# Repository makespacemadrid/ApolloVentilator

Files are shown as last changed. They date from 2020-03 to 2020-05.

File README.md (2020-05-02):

# ApolloVentilator

Information: Checkout our [wiki](https://github.com/makespacemadrid/ApolloVentilator/wiki)

### Schematic
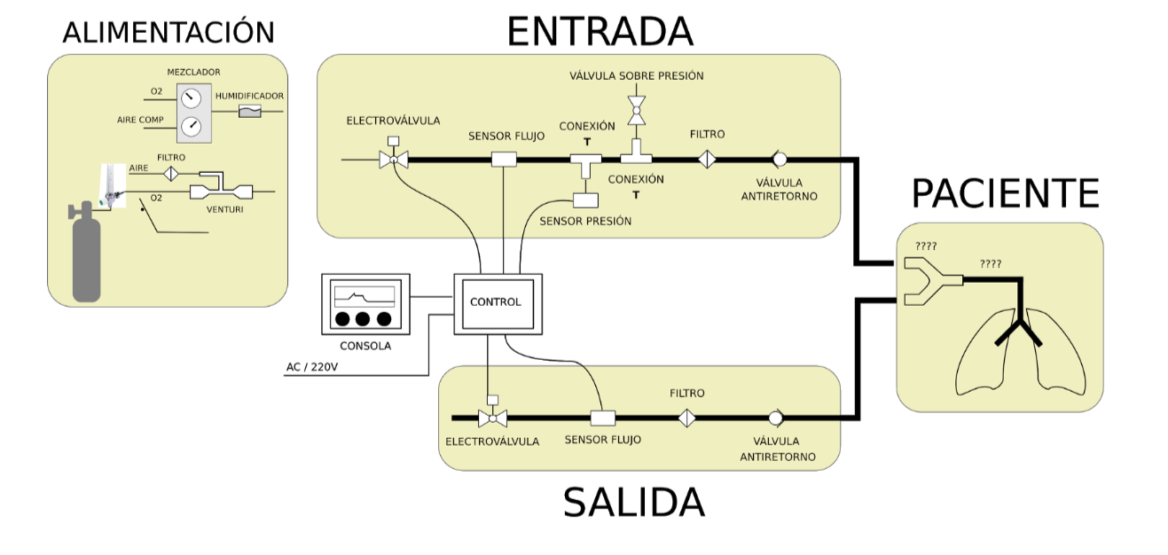
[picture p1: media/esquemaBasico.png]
Schematic


### Prototype 1 @ MakeSpace Madrid
Prototype1

### Prototype 2 @ Miguel's Workshop
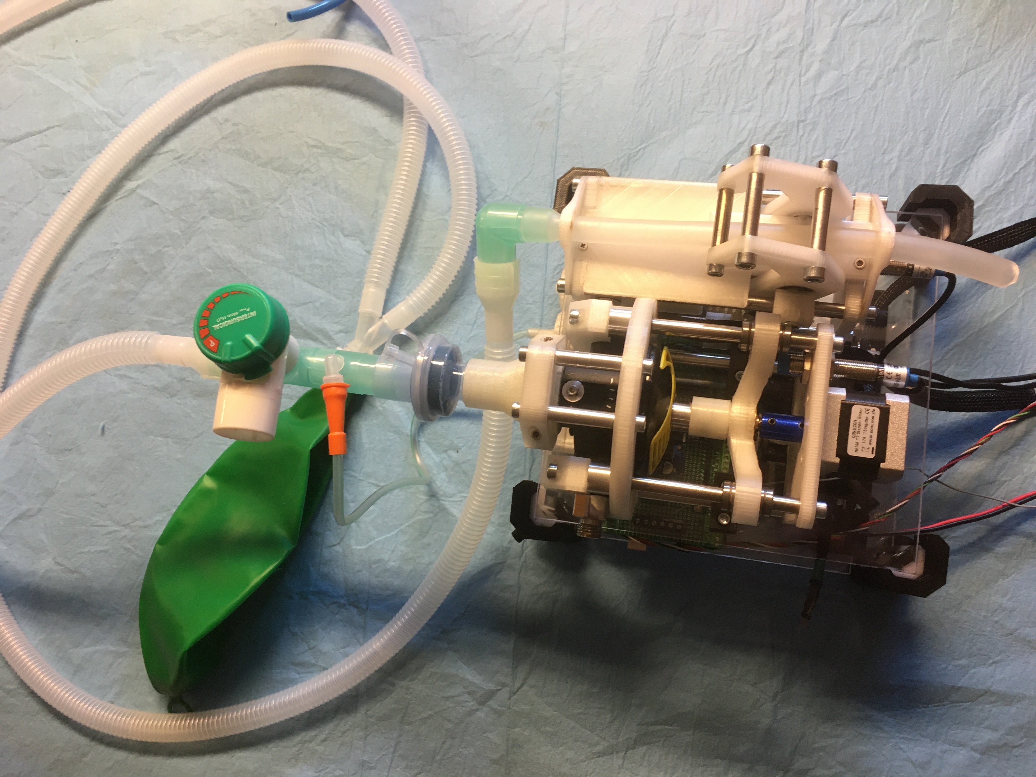
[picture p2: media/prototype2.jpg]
Prototype2


## Getting started

### Linux

```
$ apt-get install libcairo2-dev libgirepository1.0-dev python3-cairo-dev
```

### Mac

```
$ brew install pygobject3 gtk+3 libnotify
```

### App (Python 3)

From ```./gui```

Install system dependencies (Debian-based):

```
$ pip install -r requirements.txt
$ ./main.py
```

## Requirements:
2 ventilators mode
* Pressure Regulated Volume Controlled (PCV): set pressure delivered during period of inspiration. The voume measured is shown as data on display. 
* Volume Regulated Pressure controlled (VCV): The tidal volume is set and it adapts the pressure to the lowest. Here the important data are: tidal volume, upper alarm and lower current volume. Useful parameters: tidal volume, respiratory rate. There is a limit pressure and during inspiration period.

If patient stops breathing, there is a failsafe that set to mandatory breathing when it's detected.

During inspiration:

* Inspiration pressure: The plateau pressure is adjusted to volume hard limit (32 cmH2O by default, and could increate to 70cmH2O)
* Peak pressure: 2cmH2O greater than plateau.
* VCV pressure limit (15-40cm2 with increments of 5)
* Failsafe valve that opens always at 80cmH20 (or lower)

* PEEP: 5-10 with increments of 5. The circuit must be pressured.
* IE ratio: 1:1, 1:2, 1:3
* Respiratory rate: 10-30 bpm with increments of 2.
* Tidal volume: 40ml +-10, 350 +-50, 250-600 +-50,up to 8000. 
* Weight body and volume calculated based on 6ml/kg.

## Alarms

* Gas failure
* Electricity failure
* Machine switched off
* Inspiration pressure exceeded
* Inspiration pressure not achieved
* PEEP pressure not achieved
* Tidal volume not achieved
* Tidal volume exceeded
* Resistance: peak pressure - plateau pressure > 2cmH2O
* Compliance
* Volume Leakage

## Monitoring
### Settings
* Tidal volume
* Frequency
* PEEP
* FI02
* Ventilation Mode

### Current status
* Tidal volume
* Breathing rate
* PEEP
* Plateau pressure
* FI02

The normal healthy O2 consuption is 250mL/min, and could be increased until, for example 500 mL/min in a sepsis.

### Parallel measures 

* Presión arteria
* Frecuencia cardiaca
* ECG
* Nivel de sedación
* Posicion del tubo e inflado del neumotaponamiento
* Intercambio gaseoso (pulsiometria SO2), capnografía y gasometrías arteriales periodicas para obtener los **índices de oxigenación** (clave para evaluar la desintubación del paciente).

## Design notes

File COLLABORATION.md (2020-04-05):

**Tracking del proyecto**

- Todas las tareas definidas deberían aparecer en el **Project** correspondiente resumiendo el requerimiento u objetivo.  
- Una vez clarificado, la tarjeta se puede transformar en un issue (Botón derecho en la tarjeta), permitiendo asignarle 
  responsables, milestone (sprint) y creando una rama asociada. 

**Trabajo por ramas**  

- La rama debe ir asociada a un issue, eso nos permite tener contexto de la feature + discusión en un único punto (Issues).
- Permite que otras personas colaboren al poder seguir el trabajo de uno de los miembros.
- Para facilitar el flujo de trabajo a quien vaya a comenzar, que la rama master se encuentre en un punto estable.
  - Si hay dependencias entre tareas se puede hacer branch desde la rama de la tarea padre.
 
**Features, Bugs, Etc ...**  

- Utilizar un naming común para conocer lo que se está trabajando en una rama.  

> feature/gui-make-graph-faster  
> bugfix/remove-gtk  

**Pull Request**

- Intentemos que la historia del repositorio tenga sentido

> Formato de ejemplo:  
```markdown
Issue  
- Funcionamiento del bucle de draw en interfaz QT  

Objetivo  
- Visualizar correctamente una gráfica que pinte valores que se obtienen dinámicamente (puerto serie o tty emulado).

Estado  
- La gráfica se pinta correctamente pero a los 10 segundos aparece cthulhu y te pega

Changelog  
- Añadido control QTChart
- Link Evento Serie con metodo redraw
``` 

- Antes de hacer pull request se puede hacer squash (merge) de los commits en uno solo, editando el mensaje resultante.  
> git log // Contabilizas los commits que has producido en tu rama (ej. 5)  
> git rebase -i HEAD~5  
> // Cambias todos los commits que aparecen menos el primero (borrar pick y escribir squash o 's')
> También se puede hacer en la PR

- En la PR, si se utiliza la opción de Squash y --no-ff se puede mergear el commit sin añadir commits de merge al historico.

**Formato de estilos**
- Utilizar this para acceder a las propiedades de los objetos y _ al final de cada propiedad
- Variables de entrada en los setter diferentes
- Valvles Entry y Exit
- Insufflate - Exsufflate
- http://manual.gromacs.org/documentation/5.1-current/dev-manual/naming.html#common-guidelines-for-c-and-c-code

4. Documentación

- Una vez cerrada la issue, añadir la info de interes a la wiki o referenciar a la issue si no hay tiempo.

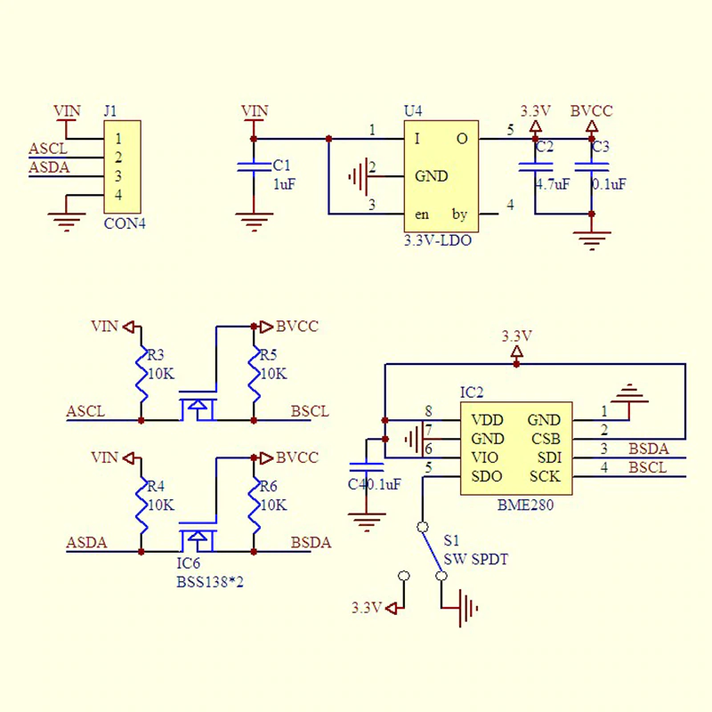
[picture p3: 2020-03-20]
Firmware/aire_apollo/doc/Gy-BME280-5V-de-alta-precisi-n-Sensor-de-presi-n-atmosf-rica-m-dulo-temperatura.jpg

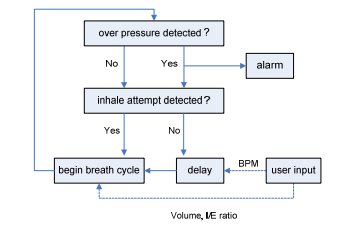
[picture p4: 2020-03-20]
media/DiagramaDeFlujo.png

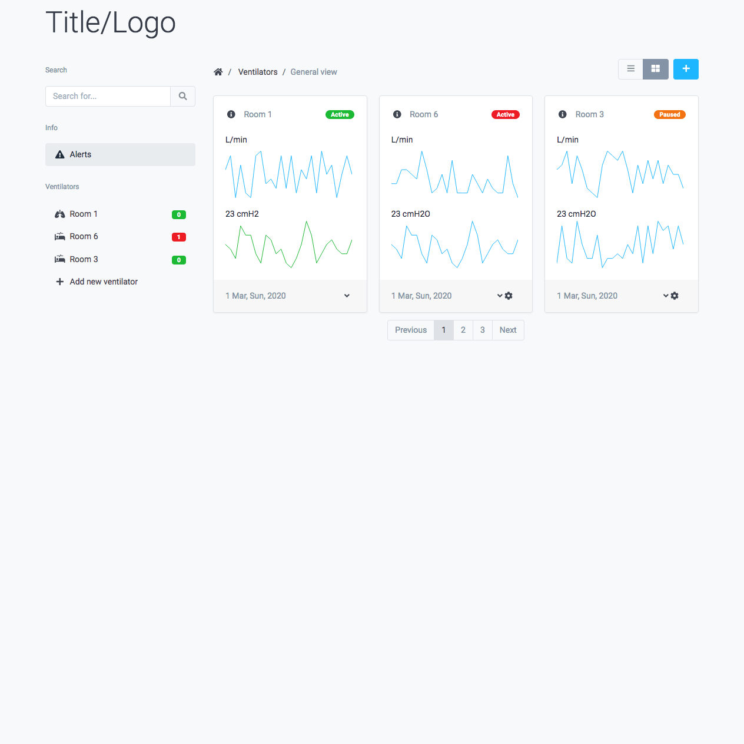
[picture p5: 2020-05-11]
gui-js/screenshots/general-grip.png

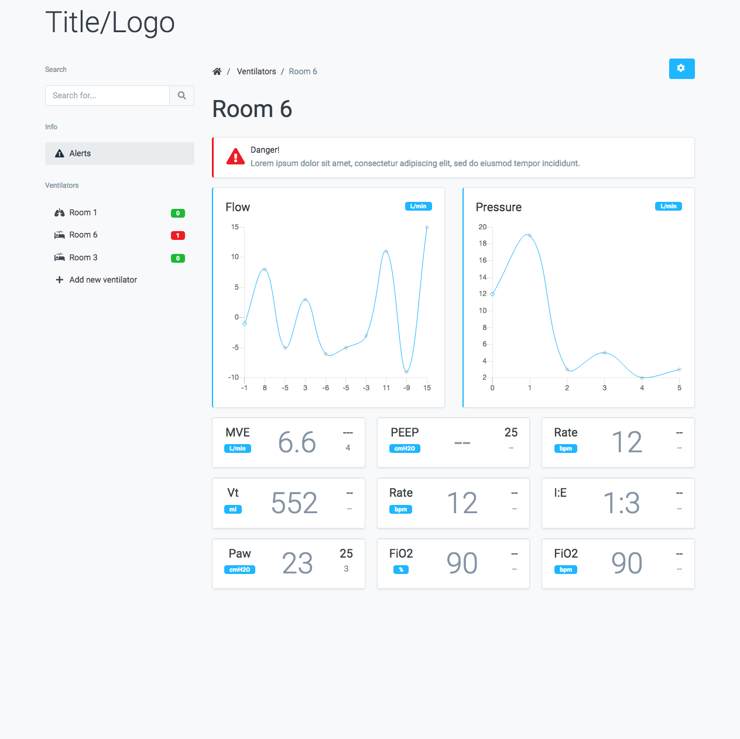
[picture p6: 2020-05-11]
gui-js/screenshots/singleView.png

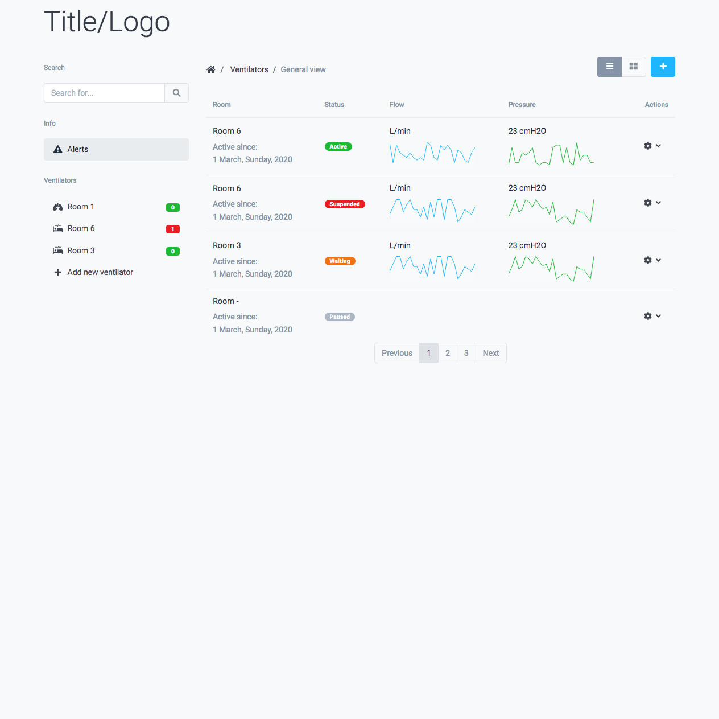
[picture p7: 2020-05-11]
gui-js/screenshots/general-list.png

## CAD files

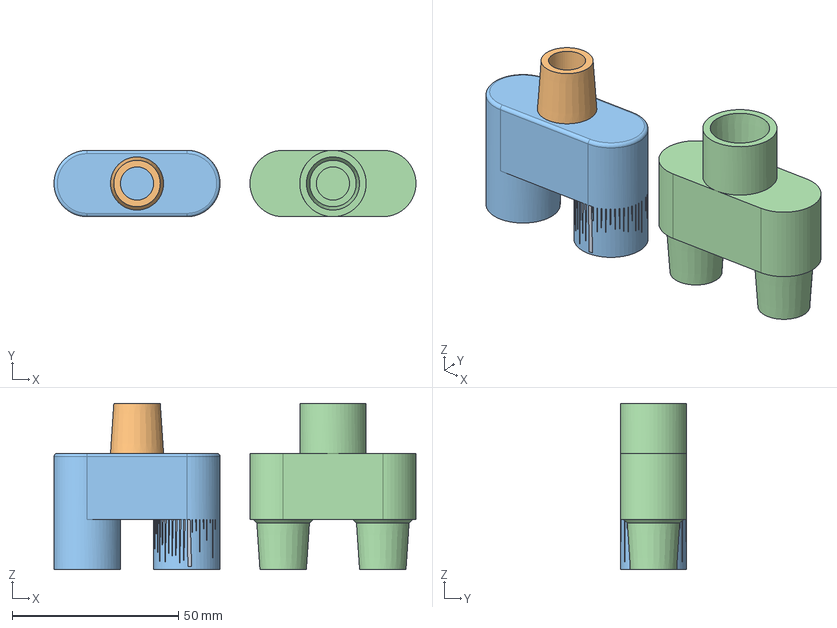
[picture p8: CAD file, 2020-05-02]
2D3D/ConectoresVarios/Y15mm.FCStd
109.0 x 20.0 x 50.0 mm

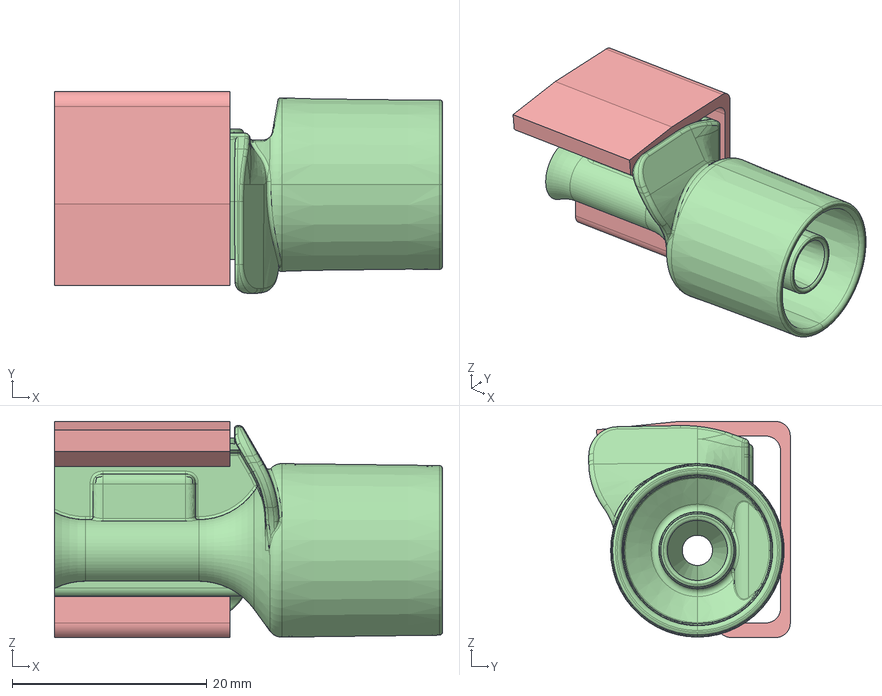
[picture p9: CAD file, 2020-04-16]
2D3D/ConnectorSensirion/v0.1.FCStd
39.8 x 20.7 x 22.2 mm

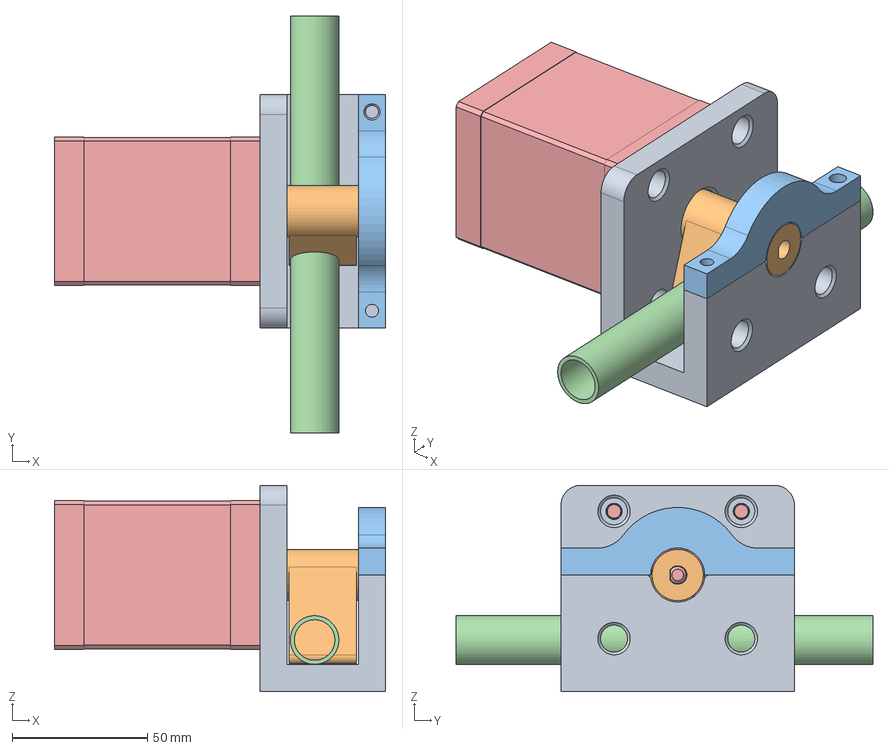
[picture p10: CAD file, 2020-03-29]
2D3D/PinchValve/it1/Válvula salida v9.step
122.5 x 154.3 x 76.4 mm
Soporte
leva
Cierre
manguera
Nema_23

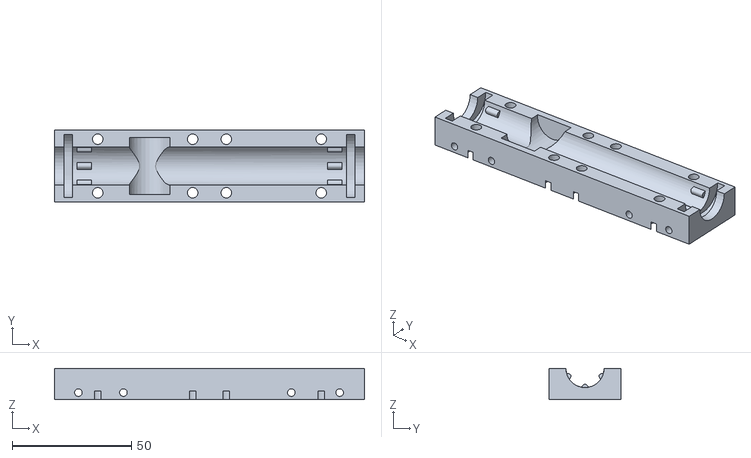
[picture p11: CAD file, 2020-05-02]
2D3D/PinchValve/it2/2/c1.stl
130.0 x 30.0 x 13.0

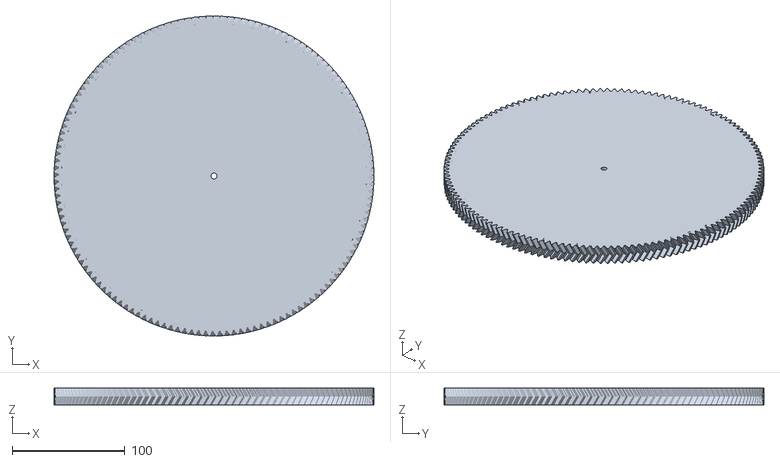
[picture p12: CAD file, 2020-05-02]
2D3D/PinchValve/it2/geargenerator2.stl
284.0 x 284.0 x 15.0

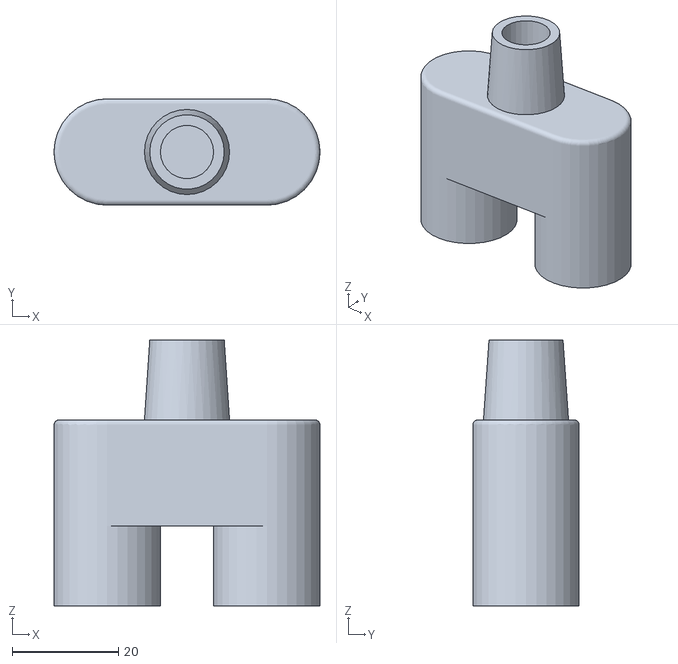
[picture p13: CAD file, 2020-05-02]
2D3D/ConectoresVarios/Y-M.stl
50.0 x 20.0 x 50.0

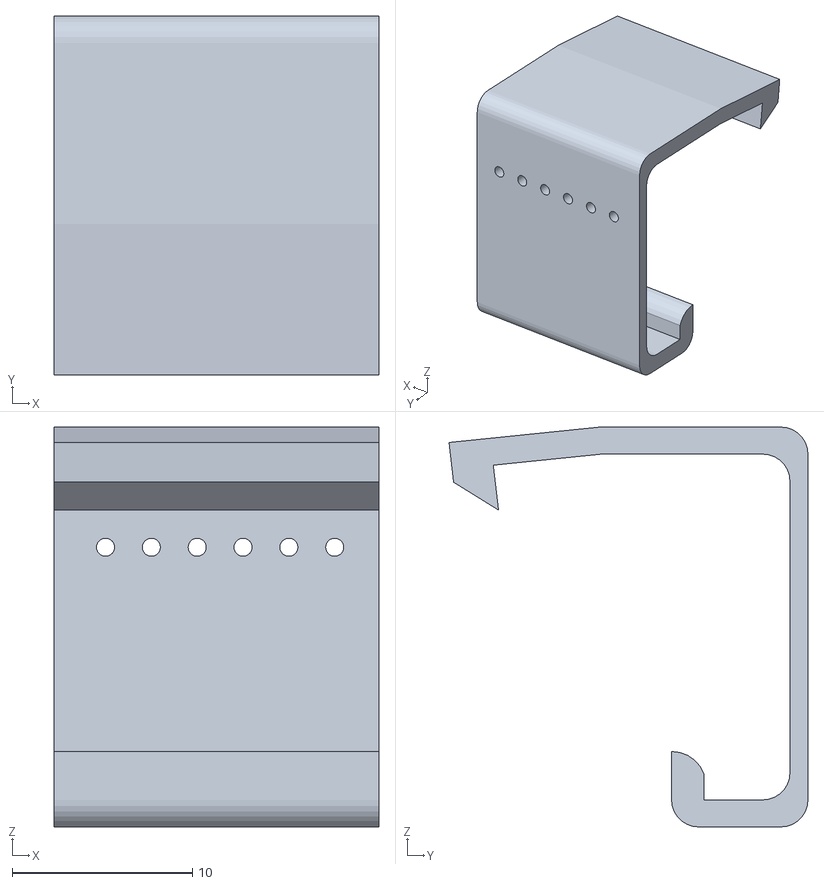
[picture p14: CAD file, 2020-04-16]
2D3D/ConnectorSensirion/clip.stl
18.0 x 19.9 x 22.2

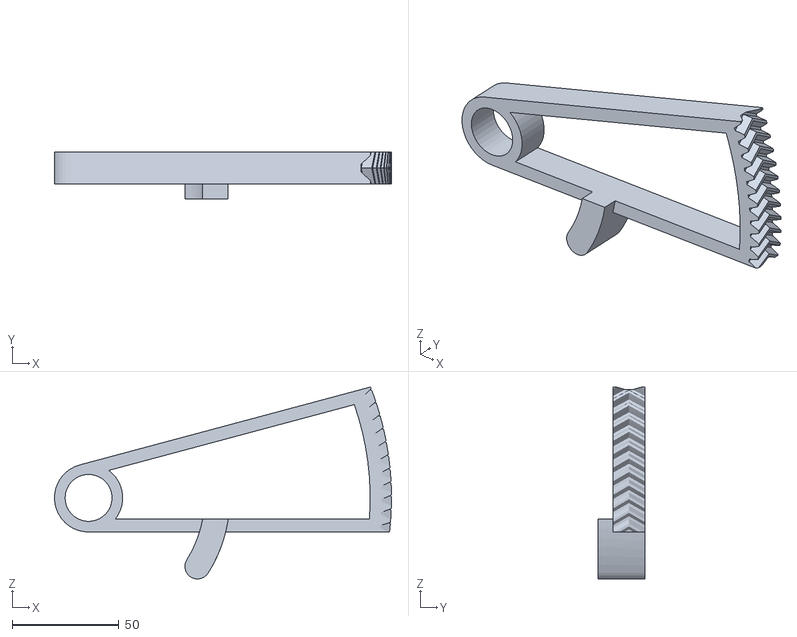
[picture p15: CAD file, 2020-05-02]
2D3D/PinchValve/it2/2/palanca.stl
158.0 x 22.0 x 90.0

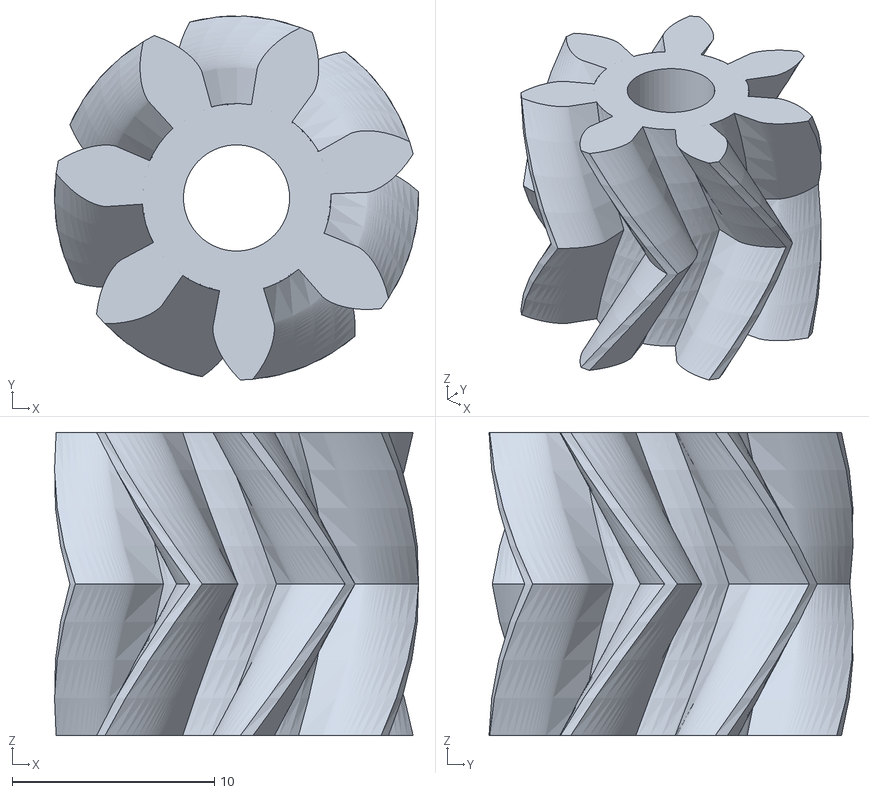
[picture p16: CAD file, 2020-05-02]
2D3D/PinchValve/it2/geargenerator1.stl
18.0 x 18.0 x 15.0

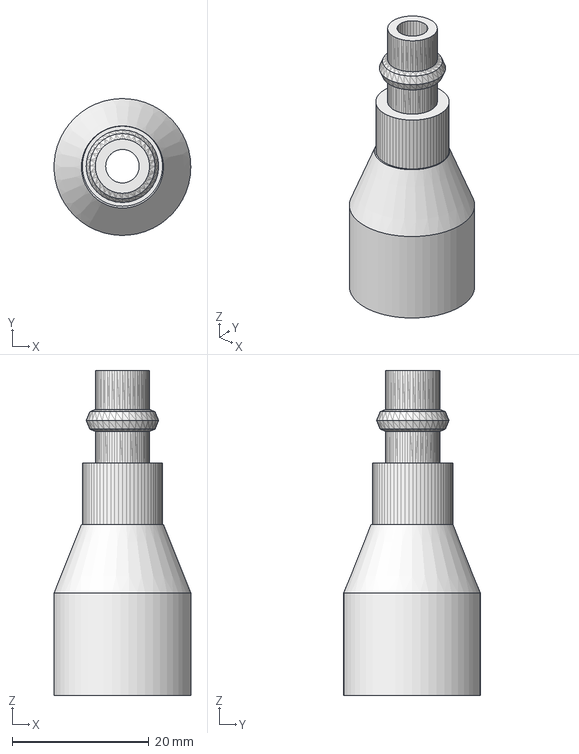
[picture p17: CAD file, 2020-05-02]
2D3D/ConectoresVarios/pneumatic15mm.FCStd
20.0 x 20.0 x 47.5 mm

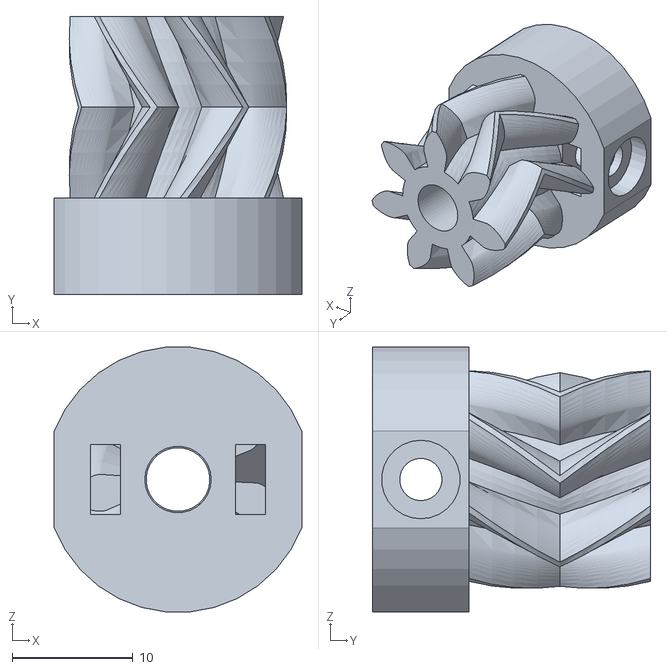
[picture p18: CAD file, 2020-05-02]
2D3D/PinchValve/it2/2/engranajeMotor.stl
20.5 x 23.0 x 21.9

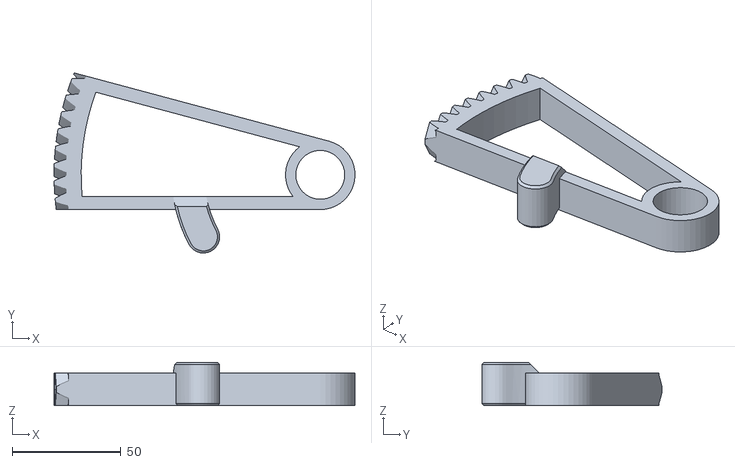
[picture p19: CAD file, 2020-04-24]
2D3D/PinchValve/it2/empujador.stl
138.5 x 82.9 x 20.0

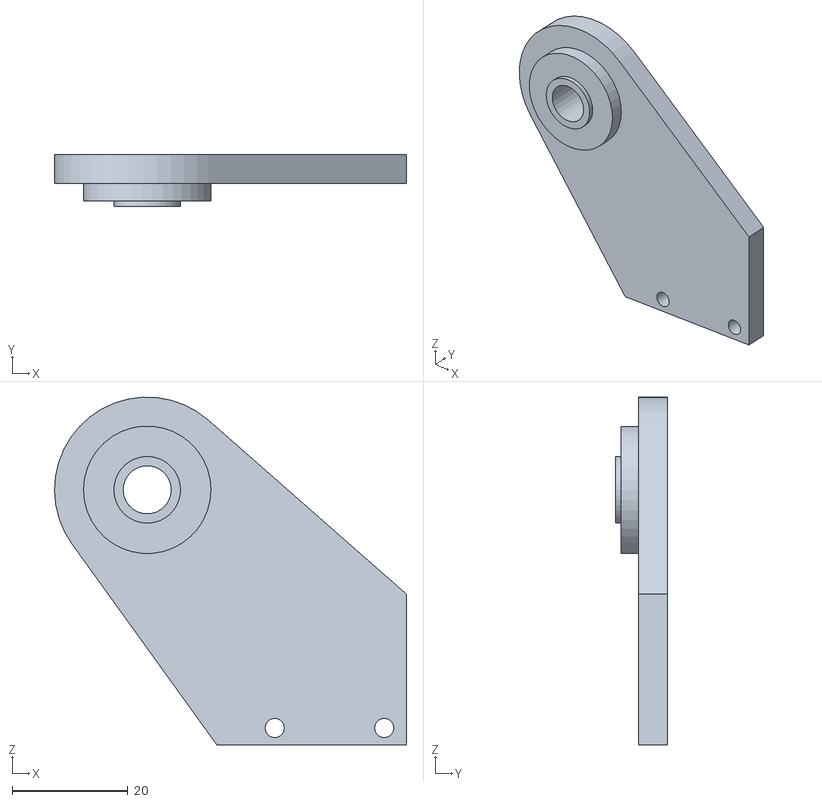
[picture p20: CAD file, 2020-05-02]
2D3D/PinchValve/it2/2/soporte1.stl
60.7 x 9.00 x 60.0

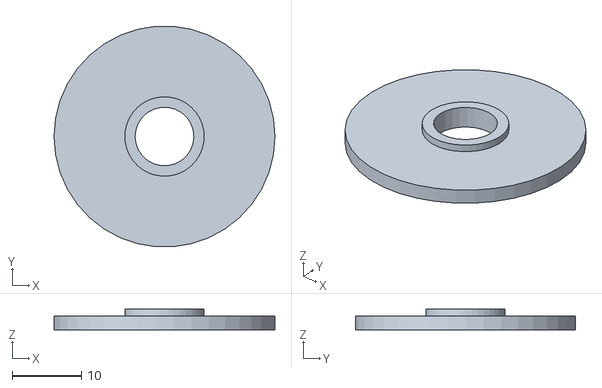
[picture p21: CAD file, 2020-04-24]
2D3D/PinchValve/it2/tapon.stl
32.0 x 31.9 x 3.00

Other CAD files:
2D3D/ConectoresVarios/Y-F.stl
2D3D/ConectoresVarios/pneumatic10mm.FCStd
2D3D/PinchValve/it2/2/c2.stl
2D3D/PinchValve/it2/cuerpo.stl
2D3D/ConectoresVarios/pneumatic10mm.stl
2D3D/ConectoresVarios/pneumatic15mm.stl
2D3D/PinchValve/it2/2/soporte2.stl
2D3D/PinchValve/it2/engranaje.stl

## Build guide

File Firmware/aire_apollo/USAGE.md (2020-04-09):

# Usage of firmware

This firmware has ben developemt using Platform IO

## Requirements
To deploy the firmware it's neccesary the next components

- [ ] Arduino Mega
- [ ] Pressure sensor
- [ ] Two valves
- [ ] Two flow sensors

If you like to enable Local Controls can add the nest components
- [ ] Display
- [ ] 3X Encoders
- [ ] Button

## Usage of firmware
1. Clone the repo and checkout the last tag
2. Edit platformio.ini if you like to use other board
3. Edit `include/defaults.h` file to update the pins that you are using
4. Edit `main.cpp` file and update the lines of initialitation of sensors and valves, with the class of your sensors and valves with the requirements parameters in constructor.

`ApolloFlowSensor *fInSensor   = new MksmFlowSensor();
  ApolloFlowSensor *fOutSensor  = new MksmFlowSensor();
  ApolloPressureSensor *pSensor = new mksBME280(BME280_ADDR);
  ApolloValve *inValve  = new StepperNema(STEPER1_ENABLE,STEPER1_DIR,STEPER1_STEP,0,0,2500,20);
  ApolloValve *outValve = new StepperNema(STEPER2_ENABLE,STEPER2_DIR,STEPER2_STEP,0,0,2500,20);
`

5. (Optional) Only if you have LocalControls enable it uncomment `#define LOCALCONTROLS`

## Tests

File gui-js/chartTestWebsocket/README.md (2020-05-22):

# Install dependencies
npm install

---
# Websocket server
Params:

--serialPortName="serialPortName"     default: /dev/ttyACM0

--serialPortRate="serialPortBaudRate" default: 115200

--webSocketPort="webSocketPort>       default: 8081

--verbose                             "Show log messages"

node webscoket.js --serialPortName="/dev/tty.usbserial-arduino"  --serialPortRate="115200" --webSocketPort="8081" --verbose

Showcase :

Main view      http://localhost:8081/

Full view      http://localhost:8081/full

Log view       http://localhost:8081/log

Log view WebGL http://localhost:8081/logwebl

---

# Mqtt pub client
Params:

--serialPortName="serialPortName"     default: /dev/ttyACM0

--serialPortRate="serialPortBaudRate" default: 115200

--host="mqttHost"                     default: localhost

--port="mqttPort"                     default: 1883

--topic="mqttMainTopic"               default: "ventilator/measurement/wilson"

--location="location"                 default: "Makespace"

--version="firmwareVersion"           default: 0.81

--verbose                             "Show JSON log messages"

--debug                               "Show hardware debug messages"

node mqtt.js   --serialPortName="/dev/tty.usbserial-arduino" --host="mqttHost" --port="63636" --topic="ventilator/measurement/wilson" --verbose

---

# Mqtt sub client
Params:

--host="mqttServer"                   default: localhost

--port="mqttPort"                     default: 1883

--topic="mqttMainTopic"               default: "ventilator/measurement/wilson/#"

node mqttSubscribe.js  --host="mqttHost" --port="63636" --topic="ventilator/measurement/wilson"

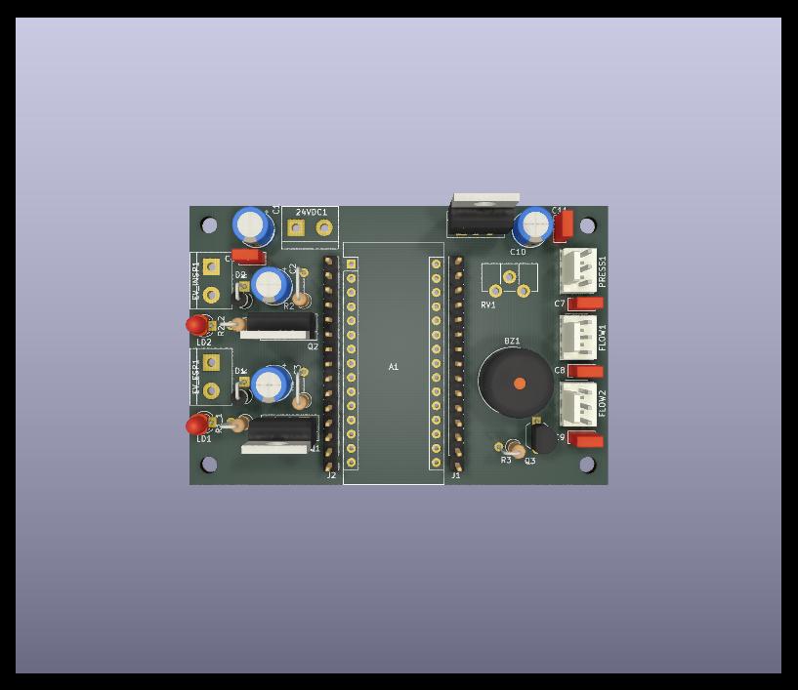
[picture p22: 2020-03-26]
hardware/testBoard/linear/aire-apollo3D.jpg

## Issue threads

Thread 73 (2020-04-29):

### ISSUE TITLE
Cambio de dirección I2C del sensor de flujo

### ISSUE THREAD

**Issue by novvere** [makespacemadrid/ApolloVentilator#73]
Crear un firmware que cambie la dirección I2C de un sensor de flujo SFM3xx.

**Comment by novvere** [comment]
El único documento que he encontrado que explica como hacerlo es para un sensor de líquidos, he preguntado al fabricante (Sensirion) como hacerlo.

**Comment by novvere** [comment]
Sensirion responde que en estos sensores no se puede cambiar la dirección I2C, hay que usar un multiplexor.

**Comment by novvere** [comment]
estamos usando una librería Software I2C para poder avanzar, tenemos que revisar los pines en los que se puede utilizar el el arduino uno. 
Si no hay dispositivo slave parece que se  bloquea, hay que revisar si se puede poner un timeout.

**Comment by novvere** [comment]
Los pines configurados para software I2C se corresponden con el número de pin dentro del puerto, es decir

```
#define SDA_PORT PORTC
#define SDA_PIN 2 
#define SCL_PORT PORTC
#define SCL_PIN 3
```

utiliza los pines A10 para SDA y A11 para SCL

Puedes definir, también antes de hacer el include..

`#define I2C_TIMEOUT 10000`

para que salte por timeout a los 10 segundos. El valor del timeout puede ir de 0 (no timeout) a 10000 (10 segundos)
En el arduino nano que Yo usé, conciden port c pin1 con A1 y portc pin2 con A2

**Comment by novvere** [comment]
No se puede cambiar la dirección del sensor y las pruebas realizadas con varias librerías I2C software dan muchos problemas. 
Optamos por usar un multiplexor  hardware

**Comment by balrog-kun** [comment]
Mientras se esperan nuevos componentes os recomiendo usar un esp32 como multiplexer.  En ESP32 tengo entendido existe I2C por hardware en los pines GPIO 21&22 pero a la libreria le dices en que pines la quieres instanciar y funciona independietemente de si son estos dos u otros, en mi prototipo usaba 3 buses I2C sin problema.

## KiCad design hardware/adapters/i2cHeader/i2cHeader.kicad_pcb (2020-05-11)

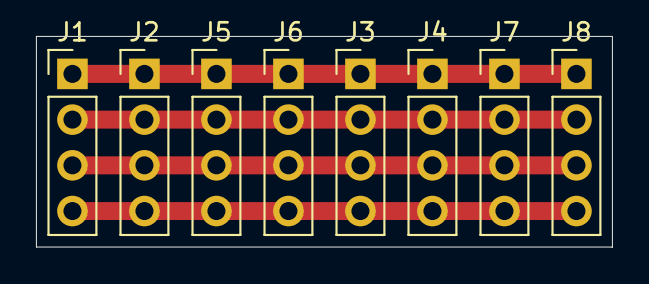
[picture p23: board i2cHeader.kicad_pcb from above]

Board: 2 copper layers, 32.0 x 11.7 mm, 8 parts (0 on the bottom side), 4 nets.

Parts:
J1, J2, J3, J4, J5, J6, J7, J8: Conn_01x04; PinHeader_1x04_P2.54mm_Vertical

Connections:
DATA: J1.3, J2.3, J3.3, J4.3, J5.3, J6.3, J7.3, J8.3
GND: J1.4, J2.4, J3.4, J4.4, J5.4, J6.4, J7.4, J8.4
SCK: J1.2, J2.2, J3.2, J4.2, J5.2, J6.2, J7.2, J8.2
VDD: J1.1, J2.1, J3.1, J4.1, J5.1, J6.1, J7.1, J8.1

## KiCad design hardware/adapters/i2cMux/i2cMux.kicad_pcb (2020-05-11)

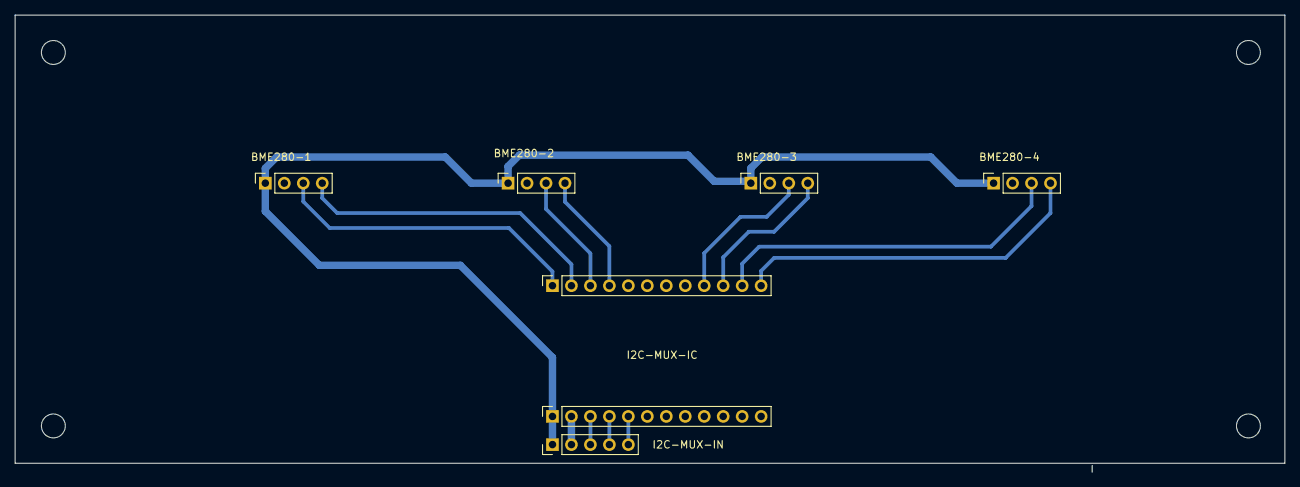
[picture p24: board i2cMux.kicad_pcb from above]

Board: 2 copper layers, 170.0 x 61.2 mm, 7 parts (0 on the bottom side), 13 nets.

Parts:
BME280-1: BME280-1; PinSocket_1x04_P2.54mm_Vertical
BME280-2: BME280-2; PinSocket_1x04_P2.54mm_Vertical
BME280-3: BME280-3; PinSocket_1x04_P2.54mm_Vertical
BME280-4: BME280-4; PinSocket_1x04_P2.54mm_Vertical
I2C-MUX-IC: I2C-MUX; PinSocket_1x12_P2.54mm_Vertical
I2C-MUX-IN: Conn_01x05; PinHeader_1x05_P2.54mm_Vertical
J2: I2C-MUX; PinSocket_1x12_P2.54mm_Vertical

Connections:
/RST: I2C-MUX-IC.5, I2C-MUX-IN.5
/SCL: I2C-MUX-IC.4, I2C-MUX-IN.4
/SDA: I2C-MUX-IC.3, I2C-MUX-IN.3
GND: BME280-1.2, BME280-2.2, BME280-3.2, BME280-4.2, I2C-MUX-IC.2, I2C-MUX-IN.2
SC2: BME280-4.3, J2.11
SC3: BME280-3.3, J2.9
SC6: BME280-2.3, J2.3
SC7: BME280-1.3, J2.1
SD2: BME280-4.4, J2.12
SD3: BME280-3.4, J2.10
SD6: BME280-2.4, J2.4
SD7: BME280-1.4, J2.2
VIN: BME280-1.1, BME280-2.1, BME280-3.1, BME280-4.1, I2C-MUX-IC.1, I2C-MUX-IN.1

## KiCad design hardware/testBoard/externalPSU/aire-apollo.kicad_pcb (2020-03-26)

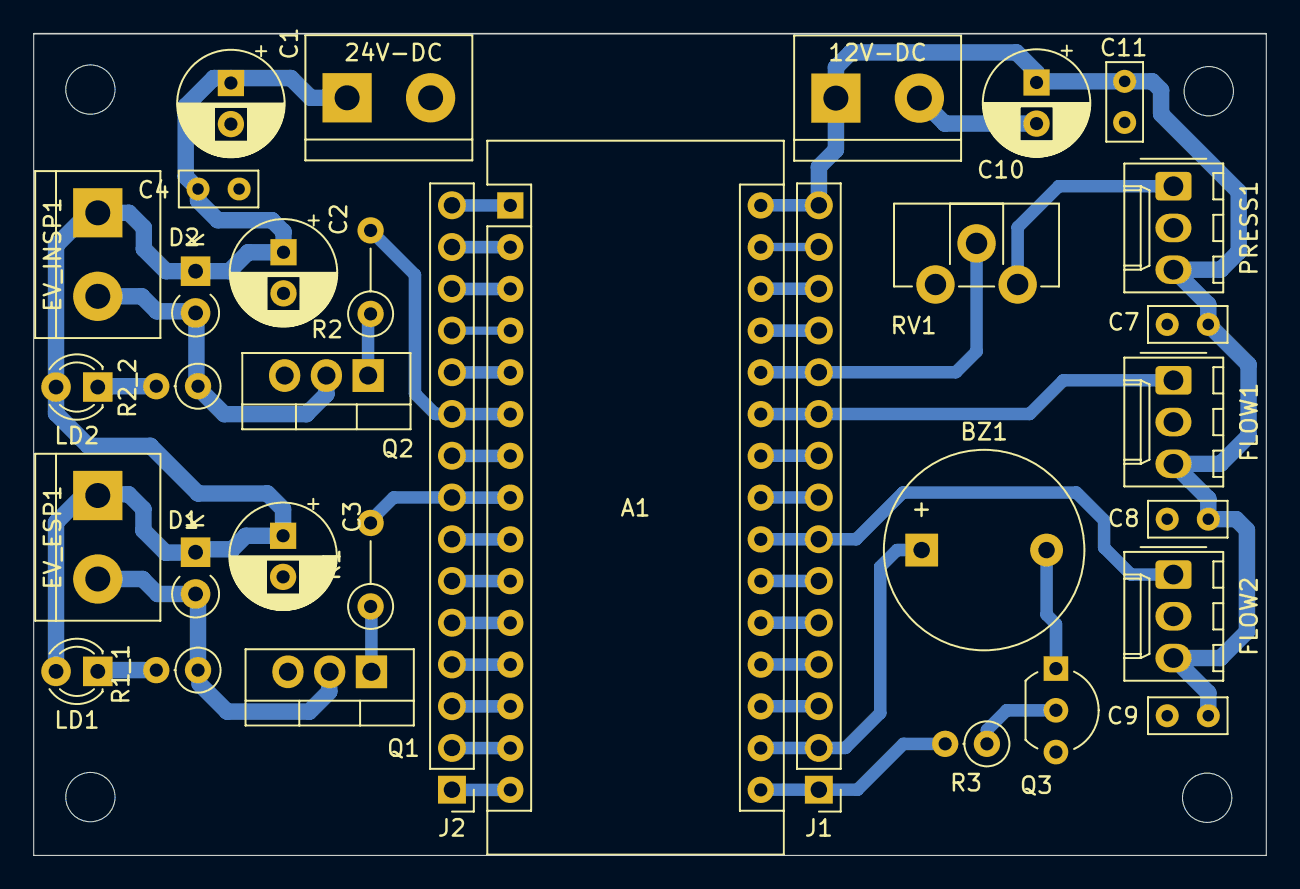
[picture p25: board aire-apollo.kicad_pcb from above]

Board: 2 copper layers, 75.0 x 50.0 mm, 33 parts (0 on the bottom side), 38 nets.

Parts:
12V-DC, 24V-DC: CON; TerminalBlock_bornier-2_P5.08mm
A1: Arduino_Nano_v3.x; Arduino_Nano
BZ1: Buzzer; Buzzer_12x9.5RM7.6
C1, C2, C3: 33uf/63V; CP_Radial_D6.3mm_P2.50mm
C4, C7, C8, C9, C11: 100nF; C_Rect_L4.6mm_W2.0mm_P2.50mm_MKS02_FKP02
C10: 100uf/16V; CP_Radial_D6.3mm_P2.50mm
D1, D2: 1N4007; D_A-405_P2.54mm_Vertical_KathodeUp
EV_ESP1: CON3; TerminalBlock_bornier-2_P5.08mm
EV_INSP1: CON2; TerminalBlock_bornier-2_P5.08mm
FLOW1: CON5; Molex_KK-254_AE-6410-03A_1x03_P2.54mm_Vertical
FLOW2: CON6; Molex_KK-254_AE-6410-03A_1x03_P2.54mm_Vertical
J1, J2: Conn_01x15; PinHeader_1x15_P2.54mm_Vertical
LD1, LD2: LED; LED_D3.0mm
PRESS1: CON4; Molex_KK-254_AE-6410-03A_1x03_P2.54mm_Vertical
Q1, Q2: TIP121; TO-220-3_Vertical
Q3: BC548; TO-92_Inline_Wide
R1, R2: 1K; R_Axial_DIN0207_L6.3mm_D2.5mm_P5.08mm_Vertical
R1_1, R2_2: 1k2; R_Axial_DIN0207_L6.3mm_D2.5mm_P2.54mm_Vertical
R3: 1K; R_Axial_DIN0207_L6.3mm_D2.5mm_P2.54mm_Vertical
RV1: 10K; Potentiometer_ACP_CA9-H2,5_Horizontal

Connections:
+12V: 12V-DC.1, A1.30, C7.1, C8.1, C9.1, C10.1, C11.1, FLOW1.3, FLOW2.3, J1.15, PRESS1.3
+24V: 24V-DC.1, C1.1, C2.1, C3.1, C4.1, D1.1, D2.1, EV_ESP1.1, EV_INSP1.1, LD1.2, LD2.2
/3V3: A1.17, BZ1.1, J1.2
/+5V: A1.27, J1.12
/A0: A1.19, J1.4
/A1: A1.20, J1.5
/A2: A1.21, J1.6
/A4: A1.23, J1.8
/A5: A1.24, J1.9
/AREF: A1.18, J1.3
/D0: A1.2, J2.14
/D1: A1.1, J2.15
/D2: A1.5, J2.11
/D4: A1.7, J2.9
/D6: A1.9, J2.7
/D7: A1.10, J2.6
/D8: A1.11, J2.5
/D9: A1.12, J2.4
/D10: A1.13, J2.3
/D11: A1.14, J2.2
/D12: A1.15, J2.1
/D13: A1.16, J1.1, R3.2
/RST: A1.3, A1.28, J1.13, J2.13
A3: A1.22, FLOW2.1, J1.7
A6: A1.25, FLOW1.1, J1.10
A7: A1.26, J1.11, RV1.2
D3: A1.6, J2.10, R2.2
D5: A1.8, J2.8, R1.2
GND: 12V-DC.2, 24V-DC.2, A1.4, A1.29, C1.2, C2.2, C3.2, C4.2, C7.2, C8.2, C9.2, C10.2, C11.2, FLOW1.2, FLOW2.2, J1.14, J2.12, PRESS1.2, Q1.3, Q2.3, Q3.3, RV1.1
unnamed: BZ1.2, Q3.1
unnamed: D1.2, EV_ESP1.2, Q1.2, R1_1.1
unnamed: D2.2, EV_INSP1.2, Q2.2, R2_2.1
unnamed: LD1.1, R1_1.2
unnamed: LD2.1, R2_2.2
unnamed: PRESS1.1, RV1.3
unnamed: Q1.1, R1.1
unnamed: Q2.1, R2.1
unnamed: Q3.2, R3.1

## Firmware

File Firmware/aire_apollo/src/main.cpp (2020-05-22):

/***************************************************************************
Apollo firmware



*Compatible Valves:
-cheap nonPWM Valves (not recommended)
-MUR servoValve (Maker Grade)
-PWM capable Valves (Depending on the valve could be Medical grade)
-Nema based pinch valve     (Maker && Medical grade)
.Nema based scuba regulator (Maker && Medical grade)

*Compatible Flow sensors:
-Interrupt based Flow sensor (use interrupt enabled pin and uncoment INTFLOWSENSOR)

*Compatible Pressure Sensors:
-BME280 (single one not recommended,no differential pressure!)
-DUAL_BME280 (Maker Grade)
-HoneywellTruStability (Medical Grade)



 ***************************************************************************/

// #define DEBUG         //Activar mensajes debug - Algo pasa con el Serial.println()
// #define INTFLOWSENSOR //Activar solo para usar los sensores de flujo por interrupcion.(NO NECESARIO PARA EL RESTO DE SENSORES DE FLUJO)



#include "../include/defaults.h"
#include "trace.h"
#include "strings.h"

//Arduino libraries
#include "Arduino.h"
#include <Wire.h>
#include <SPI.h>
#include <Adafruit_Sensor.h>
#include <Adafruit_BME280.h>
//include <FlexiTimer2.h>

//Apollo clases
#include "ApolloHal.h"
#include "Comunications.h"
#include "MechVentilation.h"
#include "ApolloConfiguration.h"
//Interfaces

//Sensors
#include "Valve/cheapValve.h"
#include "Valve/pwmValve.h"
#include "Valve/StepperNema.h"
#include "Valve/servoValve.h"
#include "Sensor/FlowSensor/MksmFlowSensor.h"
#include "Sensor/FlowSensor/Sfm3000FlowSensor.h"
#include "Sensor/Pressure/mksBME280.h"
#include "Sensor/Pressure/mksBME280diff.h"
#include "Sensor/Pressure/AnalogLinearPressure.h"
#include "Sensor/Pressure/DummyPressure.h"




int rpm     = DEFAULT_RPM;
int vTidal  = DEFAULT_MIN_VOLUMEN_TIDAL;
int porcentajeInspiratorio = DEFAULT_POR_INSPIRATORIO;


ApolloHal hal;
//MechVentilation     *ventilation;
//ApolloConfiguration *configuration = new ApolloConfiguration();
//Comunications       *com           = new Comunications(configuration);
//ApolloAlarms        *alarms        = new ApolloAlarms(com, PIN_BUZZER, true);


unsigned long lastVentilatorUpdate;


//implementar en el ventilador ??
/*
int calculateResistance(int ppeak, int pplat)
{
  return ppeak - pplat;
}

void checkLeak(float volEntry, float volExit) {}

int calculateCompliance(int pplat, int peep)
{
  return pplat - peep;
}

*/

#ifdef INTFLOWSENSOR // Gestion de los sensores de flujo por interrupcion
  void flowIn()
  {
    hal.flowIn();
  }

  void flowOut()
  {
    hal.flowIn();
  }
#endif

/*
void setRampsPWMFreq()
{//UNTESTED!
  timer 0 (controls pin 13, 4);
  timer 1 (controls pin 12, 11);
  timer 2 (controls pin 10, 9);
  timer 3 (controls pin 5, 3, 2);
  timer 4 (controls pin 8, 7, 6);

    prescaler = 1 ---> PWM frequency is 31000 Hz
    prescaler = 2 ---> PWM frequency is 4000 Hz
    prescaler = 3 ---> PWM frequency is 490 Hz (default value)
    prescaler = 4 ---> PWM frequency is 120 Hz
    prescaler = 5 ---> PWM frequency is 30 Hz
    prescaler = 6 ---> PWM frequency is <20 Hz


  int myEraser = 7;      // this is 111 in binary and is used as an eraser
  TCCR2B &= ~myEraser;   // this operation (AND plus NOT),  set the three bits in TCCR2B to 0
  int myPrescaler = 3;   // this could be a number in [1 , 6]. In this case, 3 corresponds in binary to 011.
  TCCR2B |= myPrescaler; //this operation (OR), replaces the last three bits in TCCR2B with our new value 011
}
*/
/// Porgram Begin



//uint8_t test[500];
void setup()
{
  Serial.begin(SERIAL_BAUDS);
  Serial.setTimeout(10);
  hal.debug("\nINIT");
//  alarms->begin();

/*
  ApolloConfiguration *configuration = new ApolloConfiguration();
  while (!configuration->begin())
  {
    com->debug("setup", "Esperando configuración");
  }
  com->debug("setup", "Configuración recibida");
  Serial.println("CONFIG END");
*/

//Valvulas

//  ApolloValve* inValve  = new servoValve(ENTRY_EV_PIN,0,80);
//  ApolloValve* outValve = new servoValve(EXIT_EV_PIN,2,75);
  StepperNema *inStepper  = new StepperNema(STEPPER1_STEP,STEPPER1_DIR,STEPPER1_ENDSTOP, STEPPER1_ENABLE , STEPPER1_ENABLE_STATE ,STEPPER1_STEPS_PER_RPM);
  inStepper->setMinEndStopPressedState(STEPPER1_ENDSTOP_PRESSED_STATE);
  #ifdef STEPPER1_ENDSTOP_PULLUP
    inStepper->enableMinEndstopPullup();
  #endif
  inStepper->setMaxRPM(STEPPER1_MAX_RPM);
  inStepper->setMicrosteps(STEPPER1_MICROSTEPS);
  inStepper->setOpenPos(STEPPER1_OPEN_POS);
  inStepper->setClosedPos(STEPPER1_CLOSED_POS);

  StepperNema *outStepper = new StepperNema(STEPPER2_STEP,STEPPER2_DIR,STEPPER2_ENDSTOP, STEPPER2_ENABLE, STEPPER2_ENABLE_STATE, STEPPER2_STEPS_PER_RPM);
  outStepper->setMinEndStopPressedState(STEPPER2_ENDSTOP_PRESSED_STATE);
  #ifdef STEPPER2_ENDSTOP_PULLUP
    outStepper->enableMinEndstopPullup();
  #endif
  outStepper->setMaxRPM(STEPPER2_MAX_RPM);
  outStepper->setMicrosteps(STEPPER2_MICROSTEPS);
  outStepper->setOpenPos(STEPPER2_OPEN_POS);
  outStepper->setClosedPos(STEPPER2_CLOSED_POS);

  ApolloValve *inValve  = inStepper;
  ApolloValve *outValve = outStepper;

  hal.addValves(inValve,outValve);

//Sensor Presion
  ApolloPressureSensor *pSensor = new mksBME280();

  hal.addPressureSensor(pSensor);

//Sensores de FLOW
//  ApolloFlowSensor     *fInSensor   = new Sfm3000FlowSensor(100,0x40);
//  ApolloFlowSensor     *fOutSensor  = new Sfm3000FlowSensor(100,0x40);

//  hal.addFlowSensors(fInSensor, fOutSensor);

  hal.debug("BEGIN HAL!");
  while (!hal.begin())
  {
    hal.debug("HAL BEGIN ERR!"); // No arrancamos si falla algun componente o podemos arrancar con algunos en fallo?
    delay(5000);
    //alarma!!
  }

//  while (!hal.test())
//  {
//    hal.debug("HAL TEST ERR!"); // No arrancamos si falla algun componente o podemos arrancar con algunos en fallo?
//    delay(1000);
    //alarma!!
//  }

//  while (!hal.calibrate())
//  {
//    hal.debug("HAL CALIBRATION ERR!"); // No arrancamos si falla algun componente o podemos arrancar con algunos en fallo?
//    delay(1000);
    //alarma!!
//  }


  hal.debug("HAL READY!");

//  ventilation = new MechVentilation(hal, configuration, alarms);


  unsigned long now = millis();
  lastVentilatorUpdate = now;


  #ifdef INTFLOWSENSOR
    attachInterrupt(digitalPinToInterrupt(ENTRY_FLOW_PIN), flowIn, RISING);
    attachInterrupt(digitalPinToInterrupt(EXIT_FLOW_PIN), flowOut, RISING);
  #endif

  hal.debug("SETUP COMPLETED!: " +String(now)+" ms");

}

uint16_t loops;
unsigned long lastLoopTimer = 0;

void loop()
{


  //Serial.println("loop!"+String(tim)); Serial.flush();delay(10);

  //Comprobacion de alarmas

  //  ppeak = getMetricPpeak();
  //  pplat = getMetricPplat();

  //  calculateResistance(ppeak, pplat);

  //  if (ppeak > 40)
  //  {
  //    com.alert("PRESSURE ALERT");
  //  }

  //  int peep = getMetricPeep();
  // ¿se debe meter la detección de perdidas en el hal?
  //  float volExit = hal->getMetricVolumeExit();
  //  checkLeak(volc, volExit);
  //  calculateCompliance(pplat, peep);


  hal.update();

  unsigned long now = millis();

  if(now >= lastVentilatorUpdate + VENTILATOR_INTERVAL)
  {
    lastVentilatorUpdate = now;
//    ventilation->update();
//    alarms->check();
  }

}

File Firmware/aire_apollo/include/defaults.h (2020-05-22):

#ifndef DEFAULTS_H
#define DEFAULTS_H
#include "Arduino.h"


//TIMERS
#define SENSORS_INTERVAL        25 //milliseconds
#define TELEMETRY_INTERVAL      50 //milliseconds
#define VENTILATOR_INTERVAL     100 //milliseconds
#define COMMUNICATIONS_INTERVAL 500 //milliseconds

//------HardWare---------
#define NO_PIN -1
#define ENTRY_EV_PIN    NO_PIN   //Valvula - Entrada
#define EXIT_EV_PIN     NO_PIN  //Valvula - Salida
#define ENTRY_FLOW_PIN  NO_PIN   //Sensor de Flujo - Entrada
#define EXIT_FLOW_PIN   NO_PIN   //Sendor de Flujo - Salida

//STEPPER 1 CONFIG

#ifndef STEPPER1_ENABLE //ENABLE pin
  #define STEPPER1_ENABLE -1
#endif

#ifndef STEPPER1_ENABLE_STATE
  #define STEPPER1_ENABLE_STATE LOW
#endif

#ifndef STEPPER1_DIR
  #define STEPPER1_DIR    -1
#endif

#ifndef STEPPER1_STEP
  #define STEPPER1_STEP   -1
#endif

#ifndef STEPPER1_ENDSTOP
  #define STEPPER1_ENDSTOP -1
#endif

#ifndef STEPPER1_ENDSTOP_PRESSED_STATE
  #define STEPPER1_ENDSTOP_PRESSED_STATE HIGH
#endif

//comentar/descomentar segun se necesite
#define STEPPER1_ENDSTOP_PULLUP

#ifndef STEPPER1_MAX_RPM
  #define STEPPER1_MAX_RPM 200
#endif

#ifndef STEPPER1_STEPS_PER_RPM
  #define STEPPER1_STEPS_PER_RPM 160
#endif

#ifndef STEPPER1_MICROSTEPS
  #define STEPPER1_MICROSTEPS 8
#endif

#ifndef STEPPER1_OPEN_POS
  #define STEPPER1_OPEN_POS 200
#endif

#ifndef STEPPER1_CLOSED_POS
  #define STEPPER1_CLOSED_POS 575
#endif

////////// STEPPER 2 CONFIG
#ifndef STEPPER2_ENABLE //ENABLE pin
  #define STEPPER2_ENABLE -1
#endif

#ifndef STEPPER2_ENABLE_STATE
  #define STEPPER2_ENABLE_STATE LOW
#endif

#ifndef STEPPER2_DIR
  #define STEPPER2_DIR    -1
#endif

#ifndef STEPPER2_STEP
  #define STEPPER2_STEP   -1
#endif

#ifndef STEPPER2_ENDSTOP
  #define STEPPER2_ENDSTOP -1
#endif

#ifndef STEPPER2_ENDSTOP_PRESSED_STATE
  #define STEPPER2_ENDSTOP_PRESSED_STATE HIGH
#endif

//comentar/descomentar segun se necesite
#define STEPPER2_ENDSTOP_PULLUP

#ifndef STEPPER2_MAX_RPM
  #define STEPPER2_MAX_RPM 12
#endif

#ifndef STEPPER2_STEPS_PER_RPM
  #define STEPPER2_STEPS_PER_RPM 5400
#endif

#ifndef STEPPER2_MICROSTEPS
  #define STEPPER2_MICROSTEPS 2
#endif

#ifndef STEPPER2_OPEN_POS
  #define STEPPER2_OPEN_POS 700
#endif

#ifndef STEPPER2_CLOSED_POS
  #define STEPPER2_CLOSED_POS 1690
#endif


//#define PRESSURE_SENSOR_PIN      ??
//-------I2C--------
#define BME280_ADDR 0x76
#define BME280_ADDR_OFFSET 0x77
#define LCD_DIR     0x27 //I2C Address Display

// Pause button
#define PIN_PAUSE 99

// Valores por defecto
#define DEFAULT_ESTATURA 170 // cm
#define DEFAULT_SEXO       0 // 0: varón, 1: mujer
#define DEFAULT_ML_POR_KG_DE_PESO_IDEAL 7
#define DEFAULT_MAX_VOLUMEN_TIDAL 800
#define DEFAULT_MIN_VOLUMEN_TIDAL 240
#define DEFAULT_FLUJO_TRIGGER 3
#define DEFAULT_RPM     15
#define DEFAULT_MAX_RPM 30
#define DEFAULT_MIN_RPM 10
#define DEFAULT_POR_INSPIRATORIO 33 // %
#define DEFAULT_CMH2O_FLUX_TRIGGER_VALUE -10

#define DEFAULT_CMH20_MAX     50  //Presión máxima de seguridad
#define DEFAULT_CMH20_PICO    45  //Presión máxima regular
#define DEFAULT_CMH20_MESETA  32  //Presión mínima al insuflar
#define DEFAULT_CMH20_PEEP    14  //Presión mínima en el vaciado


#define DEFAULT_WEIGHT 80
#define DEFAULT_HEIGHT 170
#define DEFAULT_GENDER 0
#define DEFAULT_POR_FIO2 90

#define MAX_STEPPER_ERROR 0.05 //Error percent alowed when testing sttepers
#define PIN_BUZZER 53

#define SERIAL_BAUDS 921600

#endif

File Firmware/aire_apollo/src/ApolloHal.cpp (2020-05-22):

#include "ApolloHal.h"
#include <Arduino.h>
#include <pidautotuner.h>


ApolloHal::ApolloHal() :
    _constantPressurePID(&_constantPressurePIDInput , &_constantPressurePIDOutput , &_constantPressurePIDTarget , _constantPressurePIDKp , _constantPressurePIDKi , _constantPressurePIDKd , DIRECT),
    _constantFlowPID    (&_constantFlowPIDInput     , &_constantFlowPIDOutput     , &_constantFlowPIDTarget     , _constantFlowPIDKp     , _constantFlowPIDKi     , _constantFlowPIDKd     , DIRECT),
    _overPressurePID    (&_overPressurePIDInput     , &_overPressurePIDOutput     , &_overPressurePIDTarget     , _overPressurePIDKp     , _overPressurePIDKi     , _overPressurePIDKd     , REVERSE),
    _inspiratoryRisePID (&_inspiratoryRisePIDInput  , &_inspiratoryRisePIDOutput  , &_inspiratoryRisePIDTarget  , _inspiratoryRisePIDKp  , _inspiratoryRisePIDKi  , _inspiratoryRisePIDKd  , REVERSE)

{
  _inputPressureSensor  = NULL;
  _inputFlowSensor      = NULL;
  _outputFlowSensor     = NULL;
  _inputValve           = NULL;
  _outputValve          = NULL;

  _lastSensorsUpdate         =0;
  _lastTelemetryUpdate       =0;
  _lastCommunicationsUpdate  =0;
  _hwStatus = hardwareUNKNOWN;
  _lastInspiratoryValveStatus = 0;
}

ApolloHal::~ApolloHal()
{
}

void ApolloHal::addValves(ApolloValve* inputValve,ApolloValve* outputValve)
{
  _inputValve  = inputValve;
  _outputValve = outputValve;
}

void ApolloHal::addPressureSensor(ApolloPressureSensor* pressureSensor)
{
  _inputPressureSensor = pressureSensor;
}

void ApolloHal::addFlowSensors(ApolloFlowSensor* inputFlow, ApolloFlowSensor* outputFlow)
{
  _inputFlowSensor  = inputFlow;
  _outputFlowSensor = outputFlow;
}

void ApolloHal::debug(String debugmsg)
{
  Serial.print("DEBUG: ");
  Serial.println(debugmsg);
  Serial.flush();
}

void ApolloHal::sendData()
{
  unsigned long start = micros();
  sendMedicalData();
  sendValveStatus();
  uint16_t elapsed = micros() - start;
  _avgTelemetryUpdateMicros = ((_avgTelemetryUpdateMicros*5) + elapsed ) / 6.0;
  _telemetryLoops++;
}

void ApolloHal::sendMedicalData()
{
  StaticJsonDocument<MAX_JSON_SIZE> jsonOutput;
  jsonOutput[STR_JSON_TYPE] = STR_MEDICAL_DATA;

  if(_hasPressureSensor)
  {
    jsonOutput[STR_PRESSURE] = getPressure();
    jsonOutput[STR_TARGET_PRESSURE] = _pressureTarget;
  }

  if(_hasFlowSensors)
  {
    float  in  = getInputFlow();
    float  out = getOutputFlow();
    float  vol = in + out;

    jsonOutput[STR_INPUT_FLOW]  = in;
    jsonOutput[STR_OUTPUT_FLOW] = out;
    jsonOutput[STR_INPUT_FLOW_INSTANT]  = getInputInstantFlow();
    jsonOutput[STR_OUTPUT_FLOW_INSTANT] = getOutputFlow();
    jsonOutput[STR_VOLUME]     = vol;
  }

  serializeJson(jsonOutput, Serial);
  Serial.println();
}

void ApolloHal::sendValveStatus()
{
  StaticJsonDocument<MAX_JSON_SIZE> jsonOutput;
  jsonOutput[STR_JSON_TYPE] = STR_HARDWARE_INFO;

  jsonOutput[STR_INPUT_STATUS] = getInputValveStatus();
  jsonOutput[STR_INPUT_TARGET] = getInputValveTarget();

  jsonOutput[STR_OUTPUT_STATUS] = getOutputValveStatus();
  jsonOutput[STR_OUTPUT_TARGET] = getOutputValveTarget();

  serializeJson(jsonOutput, Serial);
  Serial.println();
}

void ApolloHal::sendVentilatorStatus(String errorMSG)
{
  StaticJsonDocument<MAX_JSON_SIZE> jsonOutput;
  jsonOutput[STR_JSON_TYPE] = STR_VENT_STATUS;


  enum hardwareStatus
  {
    hardwareUNKNOWN,
    hardwareOK,
    hardwareUNCAL,
    hardwareERROR,
    hardwareTESTING,
    hardwareCALIBRATION
  };

  enum ventilatorStatus
  {
    ventilatorSTOPPED,
    ventilatorRUNNING,
    ventilatorPAUSED,
    ventilatorERROR
  };

  String hwS    = "NULL";
  String ventS  = STR_ERROR; // TODO!

  switch(_hwStatus)
  {
      case hardwareUNKNOWN      : hwS = STR_UNKNOWN;    break;
      case hardwareOK           : hwS = STR_OK;         break;
      case hardwareUNCAL        : hwS = STR_UNCAL;      break;
      case hardwareERROR        : hwS = STR_ERROR;      break;
      case hardwareTESTING      : hwS = STR_TESTING;    break;
      case hardwareCALIBRATION  : hwS = STR_CALIBRATION;break;
  }

  jsonOutput[STR_HARDWARE_STATUS] = hwS;
  jsonOutput[STR_VENT_STATUS]     = ventS;
  jsonOutput[STR_ERROR_MSG]       = errorMSG;

  serializeJson(jsonOutput, Serial);
  Serial.println();
}
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

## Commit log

2020-03-20 Commit inicial
    Añadido firmware de pruebas del primer dia. No hay gran cosa, medir la presion y si baja activar la electrovalvula.
2020-03-20 añadido diagrama de flujo de funcionamiento de un respirador
2020-03-21 metrics pressure and volume
2020-03-22 print number of values parametrized
2020-03-22 Integración de pseudocodigo y configuración sensor presión
2020-03-22 Mostrar GUI con gráficas de ejemplo
    Goal
    - Ejecutar una interfaz gráfica que permita visualizar gráficos con matplotlib
    Done
    - Test from_file proof of concept
    - Show subplots in apollo proof of concept
    - Write Layout using glade
    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
2020-03-23 Mostrar GUI con gráficas de ejemplo
    - Add Template to Show device info
    - Show sample graphs into device widget
    - Remove old files
    - Plotting
    - Refactoring and merging
    - Data animation
    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
2020-03-23 Añade prefijo a la salida para separar DEBUG, DATA
2020-03-23 Añadido prefijo de alarma
2020-03-24 - Add TODOs and Finish Flow
2020-03-24 - Add TODOs and Finish Flow more
2020-03-25 new parameters in device
2020-03-26 Harware test board
    [aire-apollo.kicad_pcb, aire-apollo.sch]
2020-03-26 Clean glued main and hal
2020-03-26 Update to work with basic leds
2020-03-26 [sw] Add Send Configuration Command and Manage Debug Messages
    - Send configuration command to the device via serial port
    - Manage debug messages from the device
    Tasks
    - Add *DEBUG* case
    - Add send_command_action
    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
2020-03-27 Fix window resize better gtk layout (#26)
    * Fix for window resizing and better layout of Device window
    In this commit, we have removed the font setting, 40 points is
    a REALLY big font and made all controls gigantic. Removing that
    setting (you should really let the desktop theme decide) made
    it work as expected.
    Also, I took the liberty of creating a better layout for the controls
    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
2020-03-27 remove unnecessary device1, fix data plot
2020-03-28 Added new Honeywell TruStability SPI pressure sensor
2020-03-28 integración completa
    -puede que quede algun bug
    -Todavia queda por limpiar y ordenar.... to be continued
2020-03-28 fix filter data
2020-03-29 Set Zero in pression for sensor BME280
2020-03-29 diseño de valvula de pinza imprimible(testing)
    [Soporte.stl, Válvula salida v9.step, cierre.stl, leva.stl]
2020-03-30 Fix error in Ventilator and alert in hight pressure.
2020-03-30 fix para poder hacer pruebas
2020-03-31 gui: Read serial data in the main thread
    Drop the extra thread for serial reading. Writing will still block
    (briefly)..
2020-04-04 nuevas clases de hw valvulas
2020-04-05 limpieza de las funciones de hal que usaban los punteros a sensor y creación de los metodos necesarios para acceder a esas funciones.
2020-04-05 añadido fichero para overrides de configuracion
2020-04-05 fix status valve
2020-04-05 Created new BME differencial sensor
2020-04-06 wip, ajuste de los PIDs
2020-04-06 Valves Works
2020-04-07 Add Valve in stepper
2020-04-08 Add calibrate and offsets
2020-04-08 Add new library to analog pressure sensor
    It's important that the sensor are linear!!!!
2020-04-09 modificado: Firmware/aire_apollo/src/Valve/StepperNema.h
2020-04-09 Feaure/integration pid (#66)
    * WIP: Integration of PID
    * WIP: Integration of PID
    * Renaming
    * limpieza de las funciones de hal que usaban los punteros a sensor y creación de los metodos necesarios para acceder a esas funciones.
    * añadido fichero para overrides de configuracion
    * fix status valve
    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
2020-04-10 Add Dummy sensor
2020-04-11 stepperNema ng, changelog: -Añadida secuencia de home y test inicial.
    Despues de hacer home se va a la posicion maxima y se cuentan los pasos de vuelta. si el mecanismo y el motor están ok, sera el mismo numero de ida que de vuelta.
    -Revision del tema de velocidad:
    Para poder superar cierta velocidad en el stepper en modo asincrono hay que disponer un sistema de interrupiones mas rápido/sofisticado. Pruebas iniciales, se deja en modo sincrono para pruebas.
    -Hay un bug en la posicion inicial, va a home, de ahi a posicion de inicio y en el primer movimiento vuelve a aplicar el offset de inicio.
    -Pensamiento... La valvula de pinza cierra al avanzar mientras que la valvula de submarinismo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
2020-04-14 añadido y comprobado soporte para los sensirion sfm3xxx
    [v0.1.FCStd]
2020-04-14 añadida libreria StepperDriver
2020-04-14 New Software I2C sensor
2020-04-16 -Soporte valvula Nema -Soporte Sensirion -Pruebas y bug-hunting
    [clip.stl, v0.1.FCStd]
2020-04-16 Añadida opcion para activar los pullup en los finales de carrera listo para mergue!
2020-04-16 añadido TODO con tareas pendientes a la clase stepperNema
2020-04-17 mqtt volume data param
    [i2cHeader.kicad_pcb, i2cHeader.sch, sfm3300.kicad_pcb, sfm3300.sch]
2020-04-18 -Testing del sensor del sensor de flujo sensirion -Hackeo del sensor softSfm para que funcione(el softwire lee bien los datos pero no los offset/scale) -Mejoras en la clase de valvula. ahora hay un s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
2020-04-24 Parece que funciona
2020-04-24 Otro concepto de valvula de pinza
    [Soporte.stl, Válvula salida v9.step, cierre.stl, cuerpo.stl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]
2020-05-02 Iteracion de la valvula de pinza Conectores varios
    [Y-F.stl, Y-M.stl, Y15mm.FCStd, c1.stl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]
2020-05-02 añadidas imagenes a la portada del repo
2020-05-02 Soporte para esp32 Trabajos varios en las clases y en el hal
2020-05-06 Sistema de calibracion de la rampa de presion - Proof of concept
2020-05-10 Protocolo de comunicacion por JSON Aumentada la velocidad del serie a 921600
    Tiempo de trasmision:
    115200: 9msec
    250000: 4msec
    921600: 1msec
2020-05-11 añadida libreria autotune pid.
    La libreria original da errores de compilacion en el esp. Le he cambiado las variables min max para arreglarlo
2020-05-11 json data
    [i2cMux.kicad_pcb, i2cMux.sch]
2020-05-12 Fix steppernema nuevo env para el tercer prototipo
2020-05-15 Added I2C multiplexer to diff sensor
2020-05-15 Added Venturi flow sensor
2020-05-16 Wait for the valve to close
2020-05-16 auto calibracion del pid que gestiona la presion constante
2020-05-16 fix al sistema de sobre presion
2020-05-19 Selecciona correctamente el bus i2c
2020-05-19 prueba de pid 3
2020-05-22 Trabajos varios
    -Añadidos parametros en el defaults para todas las variables del stepper
    -ajustes a la libreria de autopid
    -ajustes al proceso de autocalibrado del pid
    -escuchar en el serie
    -implementado json command
    -implementado json hwStatus
2020-05-22 añadido script para abrir automaticamente el node
